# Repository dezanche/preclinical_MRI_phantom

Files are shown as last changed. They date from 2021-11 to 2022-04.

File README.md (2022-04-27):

# Preclinical MRI Phantom
This modular phantom is designed for system calibration and quality assurance of preclinical (animal) MRI scanners. Unlike clinical (human-sized) systems, for which the [American College of Radiology](https://www.acr.org/) has standardized the phantoms and measurements, for preclinical applications phantoms with these capabilities do not exist.
This repository contains detailed information in support of the scientific abstract presented at the [2022 ISMRM conference](https://www.ismrm.org/22m/) (#5034).
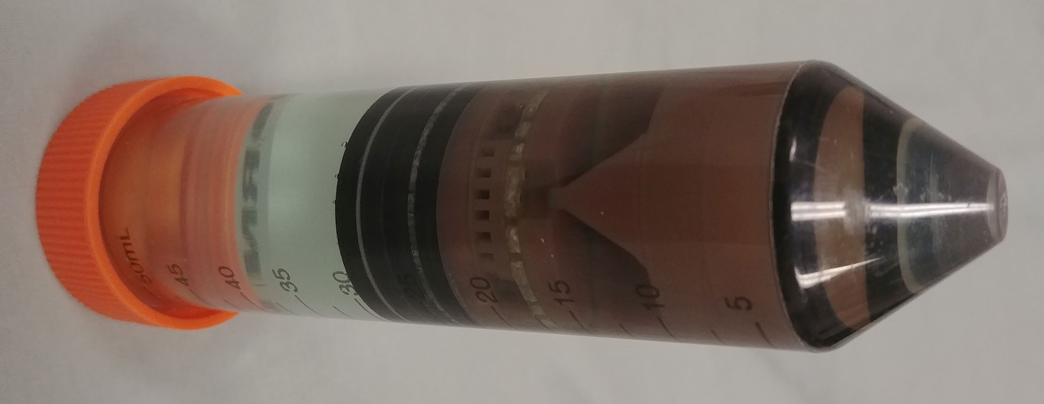
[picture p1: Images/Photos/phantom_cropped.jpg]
assembled phantom


## Contents
[CAD](https://github.com/dezanche/preclinical_MRI_phantom/tree/main/CAD) contains mechanical design (CAD) files describing the phantom as built.\
[Images](https://github.com/dezanche/preclinical_MRI_phantom/tree/main/Images) contains the renderings and photographs shown above and below.

## Construction
The phantom as built is made using an off-the-shelf 50mL centrifuge tube as the outer container (inner diameter approximately 26 mm tapering down to 25 mm at the base), in which several 25 mm diameter modules are stacked to provide the features described below. These dimensions mimic those of a mouse; to mimic other animals the dimensions of the [CAD](./tree/main/CAD) objects can be scaled accordingly to fit a container with appropriate dimensions.
The remaining volume of the container is filled with the standard 7.8 mM CuSO<sub>4</sub> and 61.6 mM NaCl aqueous solution used in the [AAPM phantoms](https://www.aapm.org/pubs/reports/rpt_100.pdf), 10 mM NiCl<sub>2</sub> and 75 mM NaCl of the [ACR phantoms](https://www.acraccreditation.org/-/media/ACRAccreditation/Documents/MRI/ACR-Large--Med-Phantom-GuidanceFinal.pdf), or other liquids that provide NMR signal.

### Modules
The modules in the [CAD](https://github.com/dezanche/preclinical_MRI_phantom/tree/main/CAD) drawing provide the following features:
1. Slice location: two sets of intersecting ramps angled at 90° to each other (tilted 45° from the axis in opposite directions).
2. Slice thickness: two sets of parallel planes tilted 10° from the transverse plane to de ne a thin slab from which the slice pro le is measured.
3. Slice angle: crossed triangular prisms to detect slice tilt (in which case the arms of the resulting cross in the image are not parallel).
4. Radial resolution: 36 radially-oriented spokes (5° wedges) taper down to 50 μm.
5. Linear resolution: two sets of rectangular slots ranging from 0.5 mm to 50 μm in width.
6. Low-contrast resolution: holes of different sizes in disks thinner than the slices acquired.
7. Distortion grid: rectangular grid of holes in a material at least as thick as the slices acquired.
8. Spacer: annulus or ring of uniform thickness maintains adjacent modules parallel and provides a region of uniform signal for measurements such as
image uniformity and SNR.

<!-- end of the list -->

modules

All modules are designed with multiple points of contact to the adjacent modules to maintain parallel alignment. To facilitate filling, modules 4 and 5
include four semicircular passages at the periphery. Care must be taken to ensure that air bubbles are not trapped in the fine features of the modules or
between modules.

modules

### Fabrication
Modules 1-5 were 3D printed using stereolithography because its resolution and fidelity (nominally 50 μm for our supplier) are superior to those of the
more common fused deposition modelling process. Modules 6 and 7 were milled using an LPKF ProtoMat S62 out of 0.8 mm FR4 (0.5 mm ⌀ holes, 1 mm
pitch) and thin (0.1 and 0.35 mm) plastic sheets, respectively. Module 7 was also made from a standard perforated prototyping printed circuit
board (FR4 without copper pads or traces) resulting in a coarser (2.54 mm pitch) grid.\
The spacer (8) is used to separate modules and to provide regions of uniform signal. In this implementation the spacers were standard R17 rubber o-
rings, but they can also be off-the-shelf nonmetallic washers, 3D printed or machined using standard techniques.
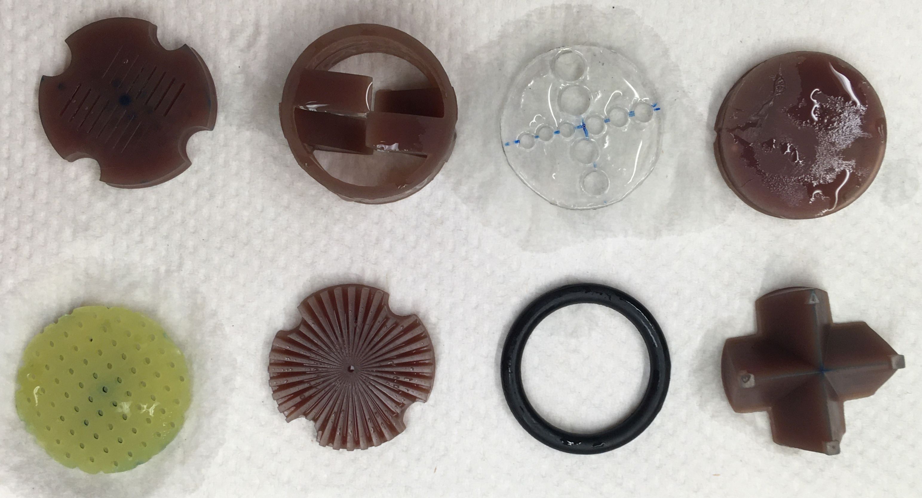
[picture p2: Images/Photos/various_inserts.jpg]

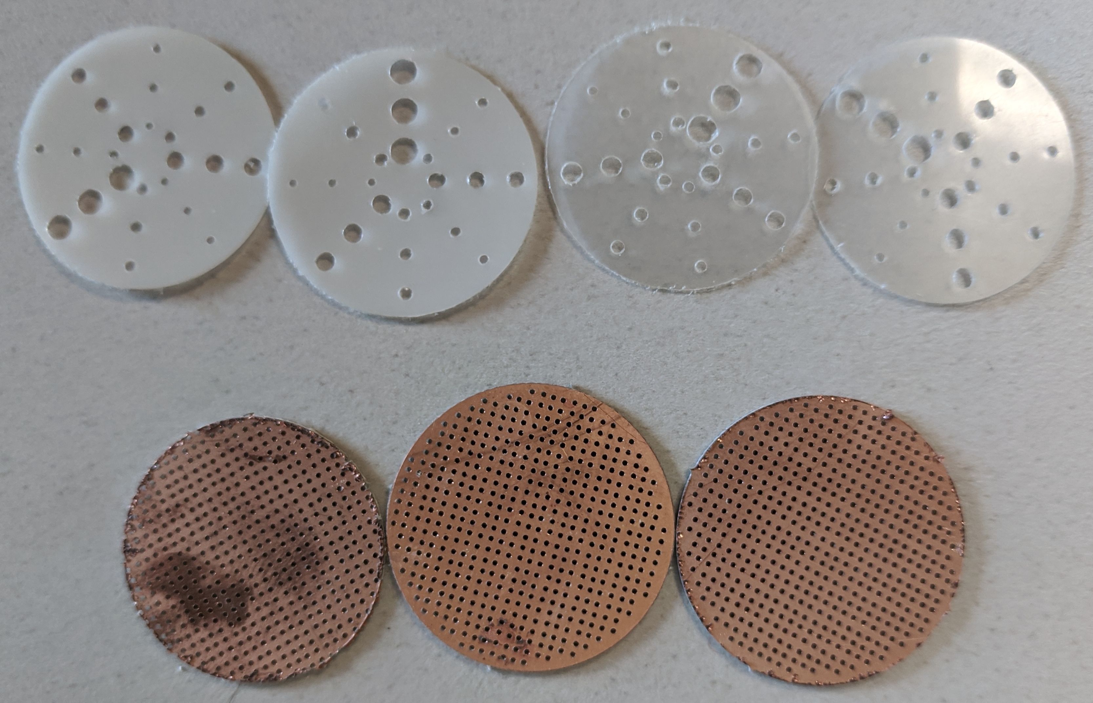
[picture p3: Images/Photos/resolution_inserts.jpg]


## Contributors
Mariko Gardiner, Anthony G. Tessier, Adam M. Maunder, Keith Wachowicz, and Nicola De Zanche.

## Licenses
[CAD](https://github.com/dezanche/preclinical_MRI_phantom/tree/main/CAD) files are licensed under the [CERN-OHL-W license](https://ohwr.org/cern_ohl_w_v2.pdf), version 2 or any later version. Additional license information is provided in that folder.\
\
All other original content in this repository (including this README file) is licensed under a [Creative Commons Attribution-NoDerivatives 4.0 International License](https://creativecommons.org/licenses/by-nd/4.0/).

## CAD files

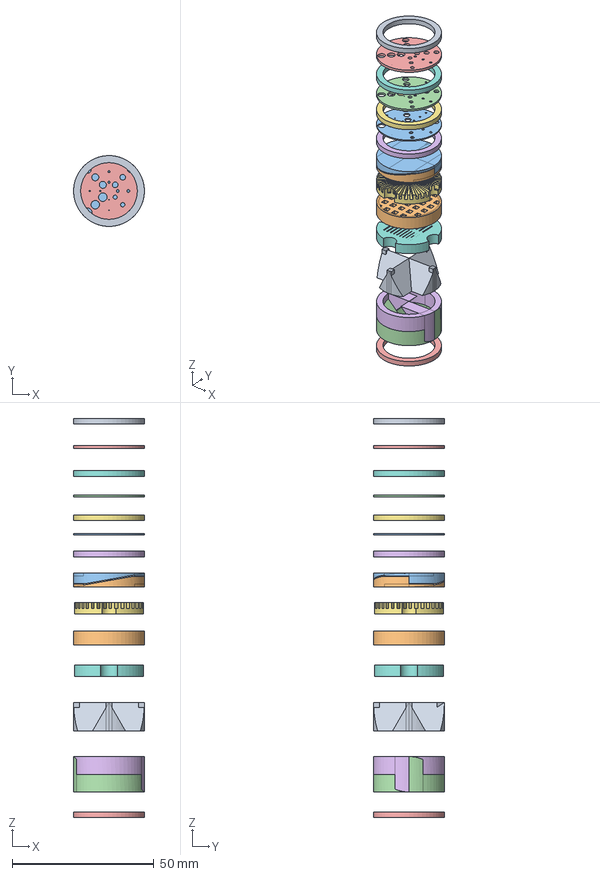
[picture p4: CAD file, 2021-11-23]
CAD/Pre-clinical_phantom_modules.FCStd
25.0 x 25.0 x 140.8 mm
spacer1
Distortion_Grid
LRT1
LRT2
LRT3
spacer004
spacer005
spacer006
Cross
STB
STT
SLB
spacer008
SLT
Radial
Comb

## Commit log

2021-11-13 CAD drawing of modules
    [Pre-clinical_phantom_modules.FCStd]
2021-11-23 new files
    [Pre-clinical_phantom_modules.FCStd, resolution_and_distortion_disks.kicad_pcb]
2021-11-23 CAD files
    [Pre-clinical_phantom_modules.FCStd, resolution_and_distortion_disks.kicad_pcb]
